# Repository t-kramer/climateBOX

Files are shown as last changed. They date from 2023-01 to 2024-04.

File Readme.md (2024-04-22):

# Welcome to the climateBOX GitHub page!

The climateBOX is a low-cost unit for personal thermal comfort monitoring.<br>
<br>
With this project we specifically aim to support novices in the field of microelectronics and help you to use the potential of low-cost sensors.<br>
<br>
Things you can find here include:

- full documentation, incl. source files for [program code](./code), [PCB](./pcb) & [housing elements](./housing)
- [building instructions](instructions.md), incl. videos
- [calibration app](https://t-kramer-revc-calibration-tool-main-mtgpng.streamlit.app) & [data](./revC-calibration) for revC velocity sensor
<br>

Also, make sure that you head to the discussions page.

https://github.com/t-kramer/climateBOX/discussions

This is where we post about any updates, ask for your feedback and host our Q&A page.<br>
<br>
<br>

Have fun!
<br>
<br>
<br>

For more information, feel free to read a scientific publication covering our thoughts around the unit's development and calibration.

*Kramer, T., Garcia-Hansen, V., & Omrani, S. (2023). climateBOX: a low-cost and open-source monitoring device for personal thermal comfort evaluation. Energy and Buildings, 112830.* https://doi.org/https://doi.org/10.1016/j.enbuild.2023.112830 



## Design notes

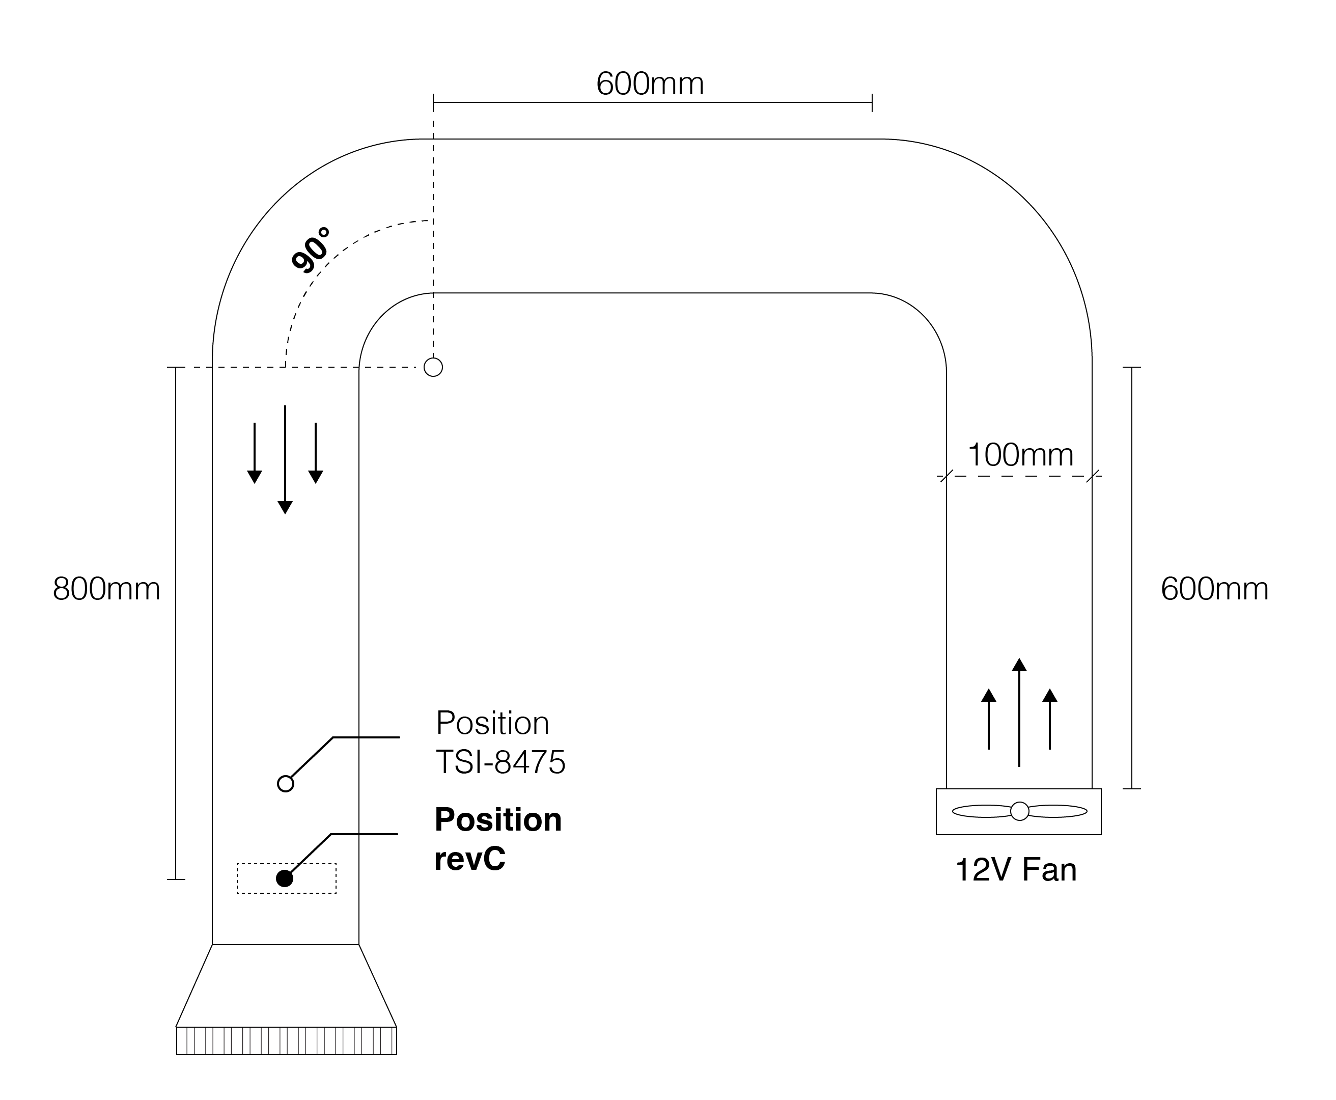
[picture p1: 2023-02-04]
img/tunnel-plan.png

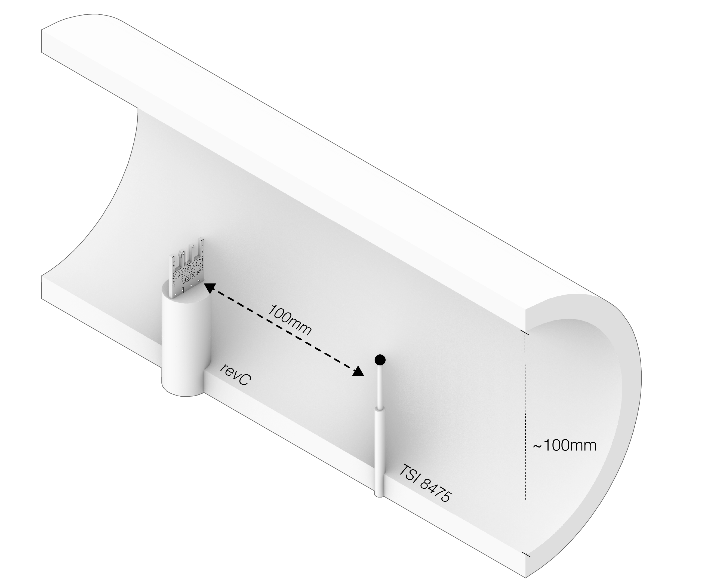
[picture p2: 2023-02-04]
img/tunnel-section.png

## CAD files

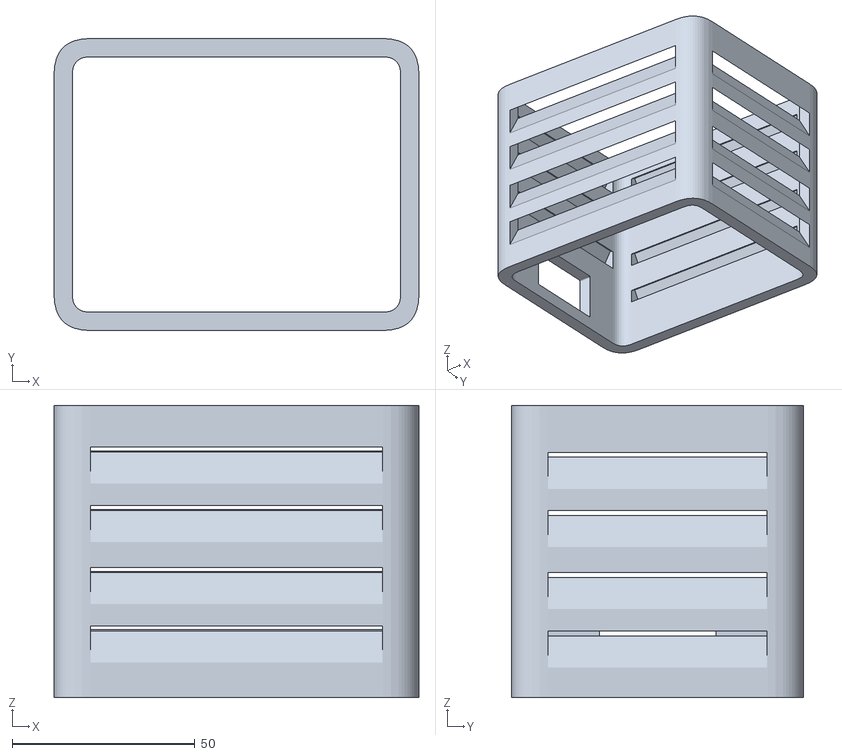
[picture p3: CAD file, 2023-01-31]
housing/stl/main-element.stl
100.0 x 80.0 x 80.0

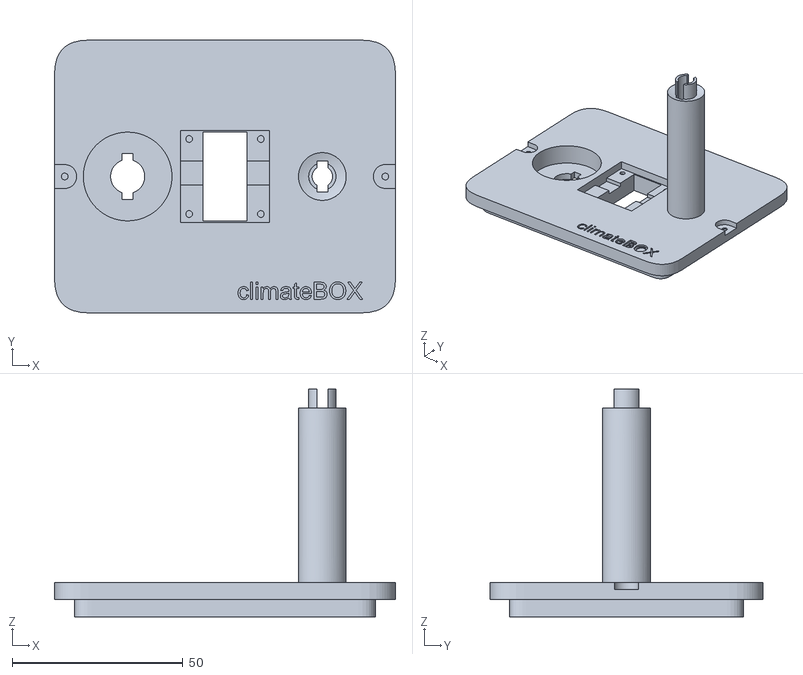
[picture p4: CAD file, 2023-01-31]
housing/stl/top-element.stl
100.0 x 80.0 x 66.7

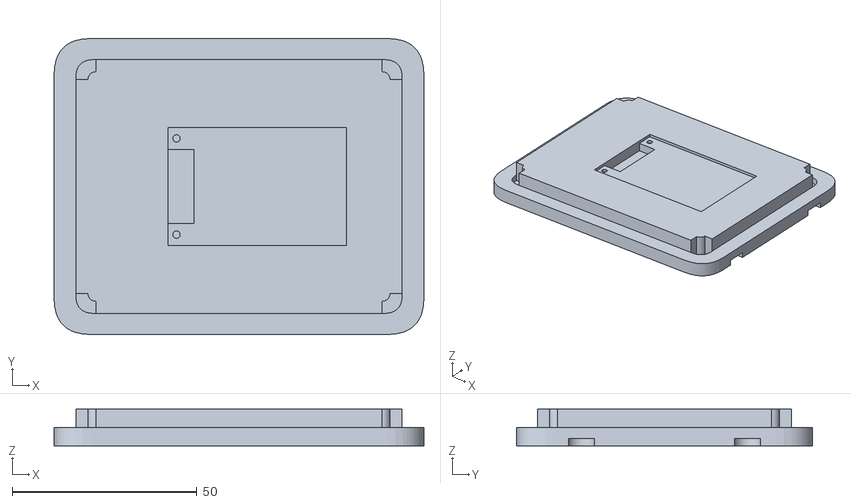
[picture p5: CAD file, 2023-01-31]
housing/stl/bottom-element.stl
100.0 x 80.0 x 10.0

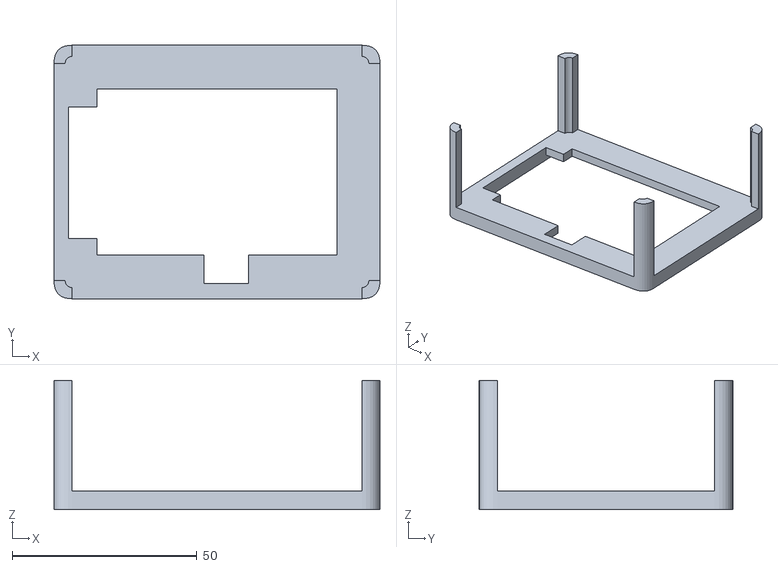
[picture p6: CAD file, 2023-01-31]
housing/stl/pcb-podest.stl
88.2 x 68.6 x 35.0

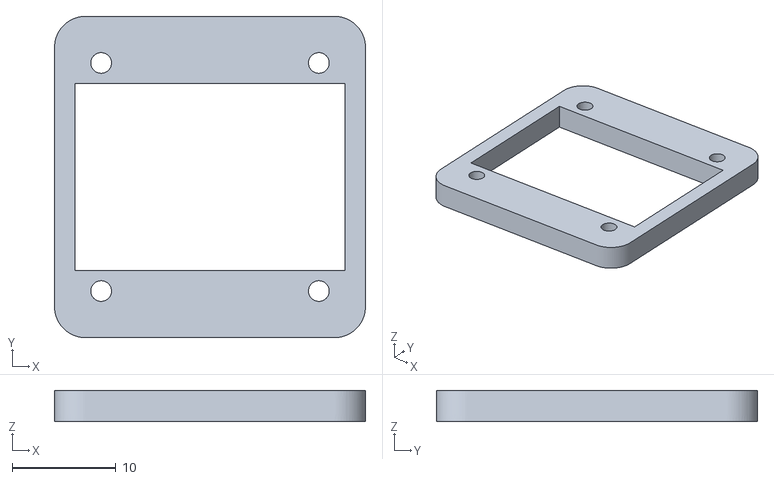
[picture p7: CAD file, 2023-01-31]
housing/stl/display-bracket.stl
30.0 x 31.0 x 3.00

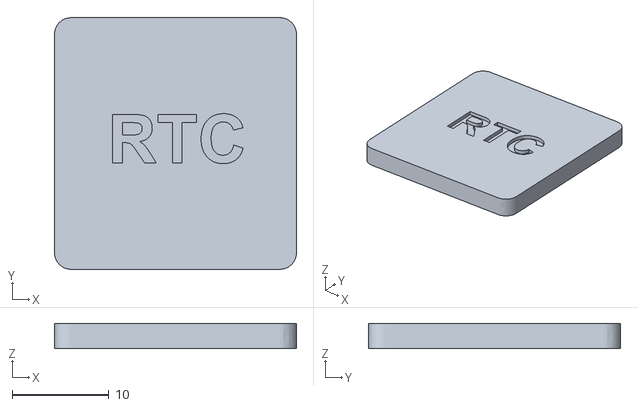
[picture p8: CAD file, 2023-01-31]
housing/stl/display-dummy.stl
25.0 x 26.0 x 2.60

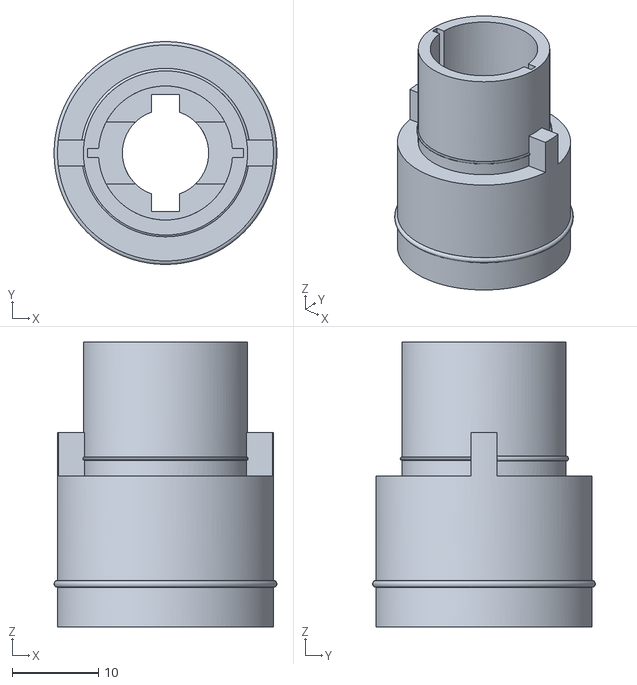
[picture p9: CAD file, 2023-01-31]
housing/stl/revC-protector.stl
25.8 x 25.8 x 33.0

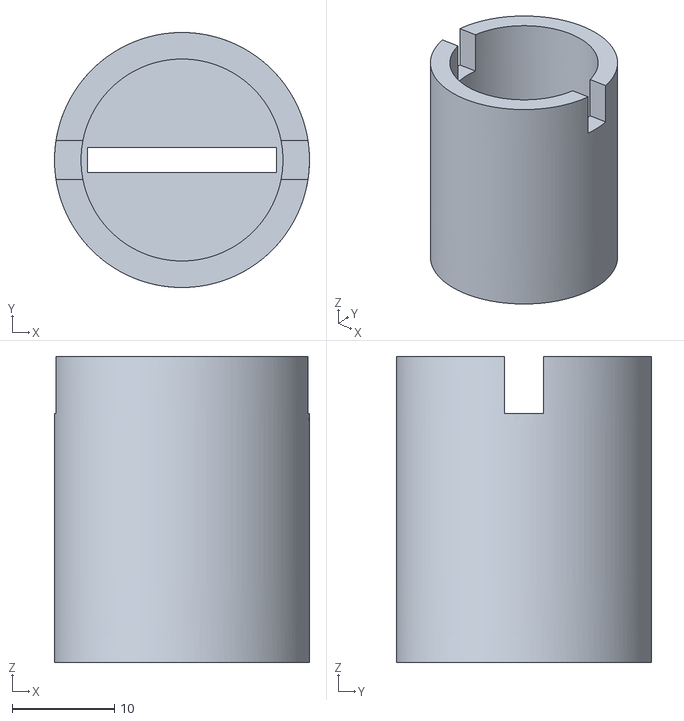
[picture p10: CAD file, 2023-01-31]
housing/stl/revc-cover.stl
25.0 x 25.0 x 30.0

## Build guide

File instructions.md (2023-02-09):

# climateBOX Building Instructions

# List of components
### a. Electronics
  1x ESP32 DevKit<br>
  1x [PCB](./pcb)<br>
  1x DHT-22<br>
  1x DS18B20<br>
  1x revC [Modern Device](https://moderndevice.com/products/wind-sensor) <br>
  1x SD module<br>
  1x RTC module*<br>
  1x OLED display*<br>
  4x 10k Ohm resistors<br>
  2x 15k Ohm resistors<br>
  1x SD card/microSD card with adapter
  1x standard micro-USB cable<br>
  1x standard 5V wall charging adapter**<br>



<br>
  
### b. Consumables
  - solder
  - stranded Wire (e.g. 22 AWG); potentially in multiple colors
  - solid core wire*
  - feather stacking headers, female
  - breakaway headers, male
  - crimp connectors + housing
  - heat shrink tubes*
  - solder wick / solder vaccuum
    

  
### c. Housing
  1x main element (side walls)<br>
  1x bottom element<br>
  1x top element<br>
  1x PCB frame<br>
  1x revC socket<br>
  1x revC cover<br>
  1x ping-pong ball, matt-black<br>
  1x display dummy* (only for v0.0)<br>
  
  [Here to Housing parts!](./housing)
  
 
  <br>

### d. Equipment
  - soldering Iron<br>
  - screw driver<br>
  - drill*<br>
  - crimping tool* (non-essential, but recommended)<br>
  - super glue*<br>

<br>
<br>
  
### e. Pre-requisites
**a) Order components**

You will not be able to build the climateBOX without the necessary components. Please stick to component list above and order them online. I can personally recommend two stores:

- https://core-electronics.com.au - Core Electronics is a good choice; generally a bit pricier, but quality equipment and fast delivery <br>
- https://au.banggood.com - Banggood is another store I can recommend; they ship internationally and are usually much cheaper; delivery takes some time though <br>

If you have questions about the components and have problems getting hands on them, feel free to send us a message and or use the discussions page. We are happy to help!
<br>
<br>

**b) Order the PCB(s)**

Before you can start building and using the climateBOX, you need to order the PCBs, or printed circuit boards. You find all require files in the [PCB](./pcb) folder

I recommend pages like https://jlcpcb.com. There are many alternatives and usually they follow the same process. You just upload the PCB files, also called “Gerber” files. This will provide the manufacturer with all essential information. You can then specify the quantity of PCBs you want to order and can make some custom configurations like changing the colour of the board etc. The price per board should be less than 2 USD.<br>
Please check the following configurations before you order:
-	Dimensions: 80mm x 60mm
-	Layers: 2

Otherwise, you should be ready to go!

*Also, if you are in Australia, feel free to contact us. We have some PCBs left and can post them.*
<br>
<br>

**c) Install Arduino IDE**

The Arduino IDE is the software we are going to use to upload the climateBOX code to the microcontroller. If you want, you can install the software before you get started with the assembly. More information can be found further below in **PART III** of the instructions.
<br>
Also, for newbies, here is a collection of useful links and tutorials that will help you with some essential vocabulary, explanations, and techniques. We will update this selection along the way.

soldering:<br>
https://core-electronics.com.au/guides/soldering-101/

stripping:<br>
https://learn.sparkfun.com/tutorials/working-with-wire/how-to-strip-a-wire

tinning:<br>
https://learn.sparkfun.com/tutorials/working-with-wire/how-to-strip-a-wire

crimping:<br>
https://core-electronics.com.au/guides/prototyping/how-to-crimp-custom-connectors/

stranded vs solid core wire:<br>
https://learn.sparkfun.com/tutorials/working-with-wire/stranded-vs-solid-core-wire

'art' of desoldering:<br>
https://www.instructables.com/How-to-Desolder-Headers/

Arduino IDE:<br>
https://core-electronics.com.au/guides/arduino-ide-tutorial/

installing ESP32 board to Arduino IDE:<br>
https://randomnerdtutorials.com/installing-the-esp32-board-in-arduino-ide-windows-instructions/
https://www.arduino.cc/en/software

installing Arduino libraries:<br>
https://docs.arduino.cc/software/ide-v1/tutorials/installing-libraries

upload program to microcontroller:<br>
https://support.arduino.cc/hc/en-us/articles/4733418441116-Upload-a-sketch-in-Arduino-IDE

<br>
<br>
<br>

  ----------------------------------
  # Step-by-Step Instructions
Now, that you hopefully have taken care of all the pre-requisites above, let’s get to the core: the actual assembly.<br>
The instructions are separated into three sections. For the first two sections, there is a helpful **video** that visualises the steps.<br> Please be aware that videos are not updated regularly and should be seen as supplementary material. **Always refer to written instructions here as the main source for documentation.**<br>
<br>
The links to the videos can be found here:<br>
<br>
[Video | Part I](https://vimeo.com/794707921)
<br>
<br>
[Video | Part II](https://vimeo.com/796140156)
<br>
<br>
Before you start, again make sure you have done the following:
- you’ve got the [PCB](./pcb)
- you have 3D-printed the [housing parts](./housing)
- you have all the components, consumables and equipment required (here we have given an asterisk * to non-essential items in the lists above)
<br>
Below you can see the circuit diagram, your main resource for building the climateBOX. Please be aware, that for v0.0 you can simply swap the OLED display for the RTC module. Both components uses the same interfaces.
<br>
circuit-diagram
<br>
The ESP32 as the microcontroller is the heart of the device. Three sensors (DHT-22, DS18B20, revC) and two additional components (SD module, OLED display/RTC module) are connected to the ESP32. Both the DHT-22 and DS18B20 require a pull-up resistor (R5, R6). As you can see, the diagram for the revC looks a bit more complicated. Here we need to do some level shifting. The revC requires around 5V to operate and provides an output signal in the same range. The ESP32 however runs on 3.3V. So to be able to use the revC output, we need to bring it down to the ESP32 operating range.
<br>
Download here:<br>
<br>
[schematic-v1.1.pdf](https://github.com/t-kramer/climateBOX/files/10541439/schematic-v1.1.pdf)

## PART I: Preparing the PCB
  
#### PCB Overview
  
<br> 

<br>
The printed circuit board (PCB) is the heart of the climateBOX. All components will be connected to the PCB, either directly soldered or via headers. We decided to use a hybrid approach in which we used headers for the sensors and the direct solder connection for other components. The obvious advantage of headers is that it is a lot easier to attach and detach components during assembly and in the case that a component needs to be replaced.<br>
<br>
The following instructions will roughly follow the order shown in the video. It is best to follow both the written instructions and the video, especially when you are new to microelectronics.<br>
<br>

**NOTE: This part is covered in video ‘climateBOX - PART I’**

<br>
Here's the link to the video again:
<br>

[Video | Part I](https://vimeo.com/794707921)

<br>
  
#### 1.1 Attaching the resistors to PCB
The first step is to attach the six resistors (4x10k Ohm,2x15k Ohm) to the PCB. For each resistor, thread both ends through the dedicated ‘through holes’ from the top side of the PCB. Then, turn the board around and fix the resistors by soldering both ends to the board.<br>
<br>
  
<br> -- IMAGE -- <br>
  
#### 1.2 Attaching female feather headers to PCB
Next, you can attach the female feather headers for the ESP32 to the PCB. Alternatively, you could also directly solder ESP32 to the PCB. However, like explained before, using headers will simplify the disassembly in case of component errors or other problems.<br>
<br>
  
<br> -- IMAGE -- <br>
  
#### 1.3 Attaching male headers to PCB
Like in the previous step, for revC and DS18b20 we opted for the flexible solution of not directly soldering these sensors or their wire ends to the PCB, but to use headers instead. In this case we used the combination of male headers on the PCB side and crimped female connecters on the sensor side. More about that in Section 2. So go ahead and solder the male pin headers to the PCB.<br>
<br>
  
<br> -- IMAGE -- <br>
  
#### 1.4 DHT-22
If you want, you can also solder the DHT-22 to the PCB directly by using the dedicated holes in the middle of the PCB. You can also use female feather headers. This will give you more flexibility when attaching/detaching the sensor.<br>
<br>

#### 1.5 RTC | Display module
Attention: If you opted for v1.0 that uses the display, I do recommend adding another set of male pin headers to the PCB. This will facilitate the assembly of climateBOX v1.0 later. This step is not covered in the video but follows the same procedure.<br>
<br>
That’s all you have to do to prepare the PCB. Next, let’s take care of the individual components and prepare them for assembly.<br>
<br>
<br>
  
## PART II: Preparing components
The following components are covered in this section:
-	globe temperature sensor (DS18B20)
-	air velocity sensor (revC)
-	SD module
<br>
Depending on the version you want to build, you have to add one additional component to this list. If you are going for v0.0, you have to prepare the RTC module. Otherwise, if you are going for v1.0, prepare the display module. Since the preparation of both modules pretty much follows the same steps covered earlier in this section, we do not cover them in the video. But you should have enough practice from previous steps to prepare these components without visual instructions.<br>
<br>

**NOTE: This part is covered in video ‘climateBOX - PART II’**

The link to the video can be found here:
<br>

[Video | Part II](https://vimeo.com/796140156)

<br>
<br>

#### 2.1 DS18B20
The DS18b20 usually comes with a relatively long cable containing three wires for power (red), ground (black) and data (white). We recommend shortening the cables/wires to around 150mm. But be careful here not to remove too much. The sensor/globe thermometer of the climateBOX sits on top of a small pole. The length of the pole needs to be included in the cable length, otherwise the cable won't be long enough, and you cannot connect it to the PCB.
<br>
  
   <br> -- IMAGE -- <br>
  
<br>
Now, after you have shortened the wires, it is time to attach the female crimp connectors. But before you can proceed you need to get rid of some insulation to expose the wires, a process called stripping. If you have never stripped a wire before, this might be of help:
<br>
https://learn.sparkfun.com/tutorials/working-with-wire/how-to-strip-a-wire
<br>
  
   <br> -- IMAGE -- <br>
  
<br>
After removing the insulation for both the main cable and the individual wires, the crimping connectors can be attached to the three wires using a crimping tool. Here, you should have a few trial runs before you actually start using the crimp connectors on the DS18B20. Again, here is a helpful link that can get you started:<br>
<br>
https://core-electronics.com.au/guides/prototyping/how-to-crimp-custom-connectors/
<br>
  
   <br> -- IMAGE -- <br>
  
  <br>
If you are satisfied with your crimping skills, go ahead apply them on the three wires.<br>
<br>
If you like it neat and tidy like me, now is the time to use some heat shrink tube to protect the exposed wires.<br>
<br>
When you are done, push the female connectors into the housing. Here, make sure that you keep the wires in the right order and that the crimped connectors are pushed deep enough into the housing until they click in properly. But be careful, as soon the connectors are locked in it can be quite hard to get them out again without breaking the plastic housing.<br>
<br>
Then you can use a hairdryer to apply the heat shrink. Done!<br>
<br>

<br> -- IMAGE -- <br>

<br>

#### 2.2 revC
Now it's time to prepare the revC. Here, we are using only four of the five pins: GND, TMP, RV, +V.<br>
<br>
The first step here is cut four wires (I recommend stranded wire, AWG22) to a length of approximately 100 mm.<br>
<br>

<br> -- IMAGE -- <br>

Stranded wire is best here because it will be exposed to some bending. Stranded wire is more flexible and is generally the best choice for most internal components.<br>
<br>
Read more about the difference between strand and solid core wire [here](https://learn.sparkfun.com/tutorials/working-with-wire/stranded-vs-solid-core-wire):
<br>
<br>
Also, colour coding makes sense here. If you have wire of different colours go ahead and use them. In the example, we used black/GND, red/V+, yellow/RV and green/TMP.<br>
<br>

<br> -- IMAGE -- <br>

Then, you can strip both ends of the wires.<br>
<br>
On one end of each wire, a female crimp connector will be attached. Here, you can go through the same process we described earlier: stripping, crimping female connectors, pushing connectors into the housing.<br>
<br>
On the other end, we need to the tin the stranded wire. The process of tinning is described under the same [link](https://learn.sparkfun.com/tutorials/working-with-wire/how-to-strip-a-wire) we used earlier.<br>
<br>
After you've completed these steps, make sure that all wires have approximately the same length. This is important for the next step. You can use a side cutter to adjust the length of the tinned wire ends.
Also, you can go ahead slip over some heat shrink over each wire. Like previously, that will later protect the soldered connections.<br>
<br>	
Now you can solder the prepared wires to the actual revC module. In the final climateBOX unit, the revC is positioned upright in a special socket (part 6+7 in the explosion graphic). Therefore, you shouldn't follow the usual process of using the through holes for the soldering connection. If you do that, the wires will be attached in a 90° angle. The socket doesn't provide enough space for that and there would be too much strain on the wire-sensor connection. Here, we will use an alternative method that allows use to solder the wires "in-parallel", which is more space-efficient in this scenario.<br>
<br>
To do that, we start by applying a big drop of solder to the solder pads to "fill" them. The solder needs to fully cover each solder pad we use, you can be generous here. Then, wire for wire, you reheat the "solder-drop" and gently push the tinned wire-ends into the melted solder drop and let it cool down to fix the connection. In the end, you only need to heat the heat shrink tubes for protection (if using). Voila, we've got ourselves a good and reliable connection.<br>
<br>
Next step SD module!
<br>
<br>

  #### 2.3 SD Module
For the SD card module the procedure is a bit different. Here we recommended a direct, non-detachable connection between SD module and PCB. Housing and PCB are designed in a way that the SD module is positioned directly under the PCB. This means we can use solid core wire, which does not need to be very flexible and saves the effort of tinning.<br>
<br>
Before you cut the wires to a length of ~40 mm, make sure that you remove any pre-installed pins from the SD module. The clean removal of pre-installed pins can be an art itself and you need to very careful here not to damage the rest of the module. [This](https://www.instructables.com/How-to-Desolder-Headers/) might be a good resource if you haven't done something like that before.
<br>
<br>
Then the process is a bit different. It makes sense to watch the video first before you go ahead, just to get the strategy. I recommend the following approach:<br>
<br>
Start and solder one end of each wire to the cleaned SD module.<br>

<br> -- IMAGE -- <br>

Then slip over some heat shrink and lead the SD module wires through the dedicated through holes on the PCB as if you were preparing to solder.<br>
<br>
After that, still keeping both components together, try to cautiously put down the PCB and SD module in the prepared housing elements. Make sure that everything is in its correct place, especially the SD module should nicely fit into the designated cavity.<br>

<br> -- IMAGE -- <br>

Now, for each through hole there should appear some remaining wire on the top side of the PCB. If this is the case, and everything is still in position, you can go ahead and solder. Afterwards, you should have some connecting wires of exactly the length you need. The last step is to use scissors or a side cutter to get rid of protruding wire on the top of PCB and apply the heat shrink below to protect the connection.<br>
<br>
<br>
<br>

  #### 2.4 RTC/Display module
Now it is time for the last component. Like we explained earlier, the component you use depends on the climateBOX version you want to build:<br>
<br>
V0.0 -> RTC<br>
<br>
V1.0 -> OLED display<br>
<br>
We can use either of these modules because they use the same PCB pins to communicate with the microcontroller.<br>
<br>
The process for both modules is roughly the same. However, we’d recommend the following: If building v0.0, directly solder the wired RTC to the bottom of the PCB. For v1.0 we use the proven combination of male header pins and female crimp connectors. We’ll quickly describe both alternatives below. But first, make sure to remove any previously installed header pins on the module you are going to use.<br>
<br>

**OLED display v1.0**

The preparation here is very similar to the revC sensor. You have to go through the process of cutting wires (AWG-22, length: ~ 100 mm), tinning (one end of each wire) and crimping (other end of the wire).<br>
<br>
After that, you can go ahead and solder the tinned ends of the wires to the OLED display module.<br>
<br>
Then push over some heat shrink if you like. Now, you can push the crimped connectors into the housing. Voila, you are done with the preparations and can assemble everything in **PART III**.<br>
<br>
<br>

**RTC v0.0**

The first steps for the RTC are similar to the ones above: cutting wires (AWG-22, length: ~ 100 mm) and tinning (both ends of each wire).<br>
<br>
Because we are going for a fixed solution here, where the RTC module is directly soldered to the PCB instead of using the detachable female connector, we save ourselves the crimping process. Just beware that a potential removal or exchange of this module later might be a bit of a tedious procedure.<br>
<br>
After tinning both wire ends, you can go ahead and solder one end of each wire to the RTC module, done! The rest will be covered in PART III.<br>
<br>
<br>

## PART III: Preparing the housing

<br>
All housing parts can be 3D printed by using the .stl files in the [housing](./housing) folder.<br>
<br>
<br>
When printed, you should go ahead and check every part for potential printing errors and test-assemble everything. The explosion graphic below shows you how to do that. 
<br>
<br>

<br>
<br>
In both, bottom and top element, there are notches. Later on, these notches accommodate a pair of screws that hold together the whole unit. We recommend to pre-drill the holes here. This will simplify the screwing process later.<br>
<br>
After you’ve done that, you can go ahead with the actual assembly.<br>
<br>
<br>

## PART IV: Assembly
Now that you've prepared all parts and finished most of the work, it's time to put everything together. <br>
<br>
But before you proceed with the final assembly and put everything into the housing, it makes sense to test the climateBOX core and its connections (soldered/crimped) before. So, I recommend dividing the assembly into two steps:
<br>

-	core assembly
-	final assembly

<br>
  
  [PICTURE]
 
#### 4.1 Core assembly
First, solder all components which do not use crimped connectors and have not been attached to the PCB yet (e.g. RTC*, DHT*) to the board. If you have followed all steps until here, you should have done that already.<br>
<br>
For the components using crimped connectors (e.g. revC, DS18b20, OLED*), you can now go ahead and attach the prepared components via the male pins previously soldered to the PCB.<br>
<br>
A quick summary of the steps and my recommended connection in brackets:
-	attach DHT-22 to PCB (soldered OR female feather headers)
-	attach DS18b20 sensor to PCB (crimped connection using male pin headers)
-	attach revC sensor to PCB (crimped connection using male pin headers)
-	v0.0: attach RTC module to PCB (directly soldered to PCB)
-	v1.0: attach OLED display module to PCB (crimped connection using male pin headers)
-	make sure SD module is soldered to PCB and SD card is inserted
-	attach ESP32 (female feather headers)

#### 4.2 Connection test
  
#### 4.2.1 The Arduino IDE
Before you go ahead with the final assembly and put everything into the housing, it makes sense to test your core connections and make sure that everything works as expected. To do that, we need to upload the climateBOX program to the ESP32 board. This can be done using the Arduino IDE, a software that allows to write and send code to the microcontroller via USB. If haven't heard about Arduino, the web has a lot of fantastic resources to dig a little deeper. The Arduino IDE is briefly described [here](https://core-electronics.com.au/guides/arduino-ide-tutorial/).
<br>
<br>
So, depending on your operating system you should head to the official Arduino website and download the IDE for Windows or Mac.<br>
<br>
https://www.arduino.cc/en/software<br>

   #### 4.2.2 Adding the ESP32 board
   The software was originally written for Arduino boards, but it does also work with the ESP32. The only thing we need to do is to manually add the ESP32 board to the board library. The following source shows you how to do that:<br>
   https://randomnerdtutorials.com/installing-the-esp32-board-in-arduino-ide-windows-instructions/<br>

 #### 4.2.3 Required libraries
To use the sensors, you also need to install some custom libraries first. Again, here is a [link](https://docs.arduino.cc/software/ide-v1/tutorials/installing-libraries) that will show you how to do that.<br>
<br>
If you are familiar with the process of installing additional libraries, please go ahead and install the following libs required to run the climateBOX:
<br>
<br>

|   Library                 | Developer         |used in:|
|---------------------------|-------------------|--------|
|   DHT sensor library      | Adafruit          | both   |
|   Adafruit Unified Sensor | Adafruit          | both   |
|   Adafruit BusIO          | Adafruit          | both   |
|   OneWire                 | Paul Stoffregen   | both   |
|   DallasTemperature       | Miles Burton      | both   |
|   RTClib                  | Adafruit          | v0.0   |
|   Adafruit SSD1306        | Adafruit          | v1.0   |
|   Adafruit GFX Library    | Adafruit          | v1.0   |
|   ESP32Time               | fbiego            | v1.0   |
|   EspMQTTClient           | Patrick Lapointe  | v1.0   |
|   PubSubClient            | Nick O’Leary      | v1.0   |

<br>
<br>

You can simply search for the name in the Arduino IDE library manager and if you are still unsure, also knowing the developer should make it easier.

<br>
<br>

  #### 4.2.4 Test Connection
Now, that all libraries are installed, the last thing we need to do upload the climateBOX program. Again, here the program you have to use depends on the climateBOX version you want to build. The programs can be found in the [code](./code) folder in this repository.<br>

<br>

If you haven’t uploaded a program to a microcontroller via the Arduino IDE yet, this [link](https://support.arduino.cc/hc/en-us/articles/4733418441116-Upload-a-sketch-in-Arduino-IDE) might be of help.
<br>
<br>

But before you upload the code to test your core assembly, it might be worth an excursion to the next section where I explain the program codes and their differences.<br>

<br>

When you have gone through the information in the next section, use the electrical circuit diagram to check all your connections once again and make sure you have connected all components in the right way.<br>

<br>

If you are confident that everything is in its correct spot, you can go ahead and connect your assembled PCB core to the computer via USB.<br>

<br>

Following the instructions in the provided link, make sure that you have selected the right board (DOIT ESP32 DEVKIT V1) and the correct port.<br>

<br>

If everything is connected properly, the core device should work as expected and described in the program code section. You can now continue with the final assembly.<br>

<br>

Otherwise, if you are having problems, first check the following, common issues:<br>
Properly check all the connections for:<br>

<br>

-	Badly soldered connections
-	Loose connections, e.g. crimp connectors not properly attached to pins
-	Component attached in a wrong way
-	Wires attached in wrong order
-	SD not inserted
-	RTC is missing battery

<br>
<br>

If neither of those things fixes your problem, feel free to navigate to the discussion page and ask. 

<br>
<br>

  #### 4.3 Final assembly
  - detach DS18b20 & revC
  - lead wires of both sensors through pre-cut holes in top element
  - click PCB with SD and RTC module into PCB podest
  - click PCB frame element into pre-cut holes in bottom element (maybe use super glue to fix connections)
  - click in DHT22 sensor into PCB designated feather headers (if not soldered)
  - slip over main wall element
  - lift top element including revC and DS18b20 sensors
  - connect sensors to PCB
  - while pushing wires into the interior of the box, push down the top element and attach by tightening screws
  - attach USB wires

<br>

assembly@2x

--------------------------------------------------
  ## Part V: The Program Code
  
  We are planning to release another video here soon.<br>
  The video will cover the following:<br>
  - general code structure
  - differences between v0.0 and v1.0
  - how to set-up a cloud monitoring system consisting of several v1.0 climateBOX units
  - FAQ, common errors and further information on things like resetting the RTC, customisations, etc.
  <br>
  <br>
  For now, please refer to the inline comments in the sketches/program files. Also, feel free to contact us if there is anything specific you want to know. :)
  <br>
  <br>
  For v0.0: If you have manually installed all libraries mentioned above, you should be able to upload and run the code without any prior knowledge and further explanations. Before you upload the code, make sure that you change the zeroWind adjustment to the value you obtained from the calibration/calibration tool. Otherwise, if you have followed the steps described earlier and the reminders below, you should be ready to go.
  
  <br>
  <br>

  - make sure that: USB wire is attached properly, SD card is inserted
  - connect climateBOX to PC/Mac via USB
  - select the correct board in Arduino IDE
  - verify and upload the climateBOX_v0.0.ino file
  - check the serial monitor for output

--------------------------------------------------
  ## OPTIONAL - Part VI: Setting up a cloud-based monitoring system (advanced)
  
  The ESP32 comes with on-board WiFi. This allows to use several v1.0 units together in a WiFi-based monitoring system with live data upload to a cloud database and/or dashboard. This facilitates the process of retrieving the data and a provides a live visualisation of collected data. Please be aware, that the v1.0 work individually without a problem and do only require WiFi access to update the time. The data is always stored on the local SD card. But who doesn't want a nice and schmick dashboard?
  <br>
  <br>
  What you need:
  <br>
  1x Raspberry Pi (e.g. 3 or 4)
  <br>
  1x 4G/LTE USB Dongle incl. SIM card from your local mobile provider
  <br>
  2+ climateBOX v1.0 units
  <br>
  
  <br>
  <br>
  
  In a minimal solution, the only things you need are a climateBOX v1.0 unit and a WiFi network. Services like Adafruit I/O make it very easy to upload microcontroller data to a live dashboard and do not really require any background knowledge. If you think that this is your preferred option, feel free to do some research on the web. There are many sources that describe how to set up such a system. Hint: The Adafruit I/O webpage would be a good start :)
  However, based on our experience we suggest an alternative solution which, to be honest, requires a little more setup, but is absolutely worth the effort.
  
  <br>
  <br>
  
  In todays world where most WiFi networks are well protected, it can be quite hard to connect your microcontrollers, especially if you want to use it for a longer period and don't want to change network SSIDs and PW everytime you setup your device in a new space. This is why we suggest to make your system completely indepedent and to bring your own network. Yes, correct. You can easily bring your own network with you.
  
  <br>
  <br>
  
  We made good experiences with using a Raspberry Pi and a common 4G USB dongle to setup our own network. Connected to the 4G/LTE mobile network via a SIM card from a local provider, the RPi acts as a hotspot all your units can be connected to. The best thing is that the IP address, network SSID and PW remain the same, wherever you want to go. This means that setting up your system in a new place is as easy as connecting everything to a power source, done!
  
  <br>
  <br>
  
  While setting up the communication between the climateBOX units, RPi and the web might take some time, this remains an initial one-time effort and usually doesn't require any maintenance or updates. The most difficult part is probably to setup the RPi. Luckily, someone made an effort to explain everything step by step:
  
  <br>
 
  LINK
  
  <br>
  <br>
  
  If you want a little more background information, it might be worth reading about [MQTT](https://mqtt.org), the communication protocoll that is used here. In our system the RPi is the MQTT broker, and the individual climateBOX units are clients. The climateBOX v1.0 code is written for use in such a system. The only things you need to adjust are the settings related to the MQTT. More on that in the additional video which will be released soon.

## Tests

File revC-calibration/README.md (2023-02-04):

Welcome to the **revC calibration** folder!

In here, you'll find two things:<br>
<br>
a) raw data gathered for the calibration of our sensors<br>
b) the **revC calibration app**
<br>
<br>
The most important thing for you will be the calibration app, which will assist you in calibrating each revC sensor you are using against a reference function.
The app is based on another repository and can be found deployed as a Streamlit app here [HERE](https://t-kramer-revc-calibration-tool-main-mtgpng.streamlit.app)!
<br>
<br>
On this page you will also find some more information about the process.

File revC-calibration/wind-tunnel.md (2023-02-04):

### Wind tunnel

To construct the wind tunnel we used some standard PVC pipes from the hardware store. The air movement was created by a simple 12V CPU with a variable DC supply to control the air speed. We are able to produce velocities of up to 2.4 m/s.

Here are some images of the concept:

tunnel-plan
tunnel-section

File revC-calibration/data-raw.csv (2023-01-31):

sensor-id | temp [¡C] | revC_raw_tmp | revC_raw_rv | tsi_value [m/s]
11 | 24 | 1.495 | 1.134 | 0
11 | 24 | 1.501 | 1.136 | 0
11 | 24 | 1.495 | 1.133 | 0
11 | 24 | 1.501 | 1.131 | 0
11 | 24 | 1.498 | 1.135 | 0
11 | 24 | 1.496 | 1.134 | 0
11 | 24 | 1.495 | 1.131 | 0
11 | 24 | 1.498 | 1.131 | 0
11 | 23.9 | 1.501 | 1.133 | 0
11 | 23.9 | 1.497 | 1.134 | 0
11 | 24 | 1.491 | 1.135 | 0
11 | 24 | 1.491 | 1.134 | 0
11 | 24 | 1.495 | 1.134 | 0
11 | 24 | 1.495 | 1.128 | 0
11 | 24 | 1.491 | 1.136 | 0
11 | 24 | 1.491 | 1.133 | 0
11 | 24 | 1.491 | 1.137 | 0
11 | 24 | 1.497 | 1.142 | 0
11 | 24 | 1.497 | 1.137 | 0
11 | 24 | 1.495 | 1.136 | 0
11 | 24 | 1.495 | 1.131 | 0
11 | 24 | 1.495 | 1.126 | 0
11 | 24 | 1.494 | 1.129 | 0
11 | 24 | 1.494 | 1.126 | 0
11 | 24 | 1.489 | 1.129 | 0
11 | 24 | 1.491 | 1.131 | 0
11 | 24 | 1.493 | 1.134 | 0
11 | 24 | 1.49 | 1.134 | 0
11 | 24 | 1.488 | 1.131 | 0
11 | 24 | 1.488 | 1.127 | 0
11 | 24 | 1.488 | 1.131 | 0
11 | 24 | 1.486 | 1.134 | 0
11 | 24 | 1.488 | 1.139 | 0
11 | 24 | 1.487 | 1.143 | 0
11 | 24 | 1.487 | 1.136 | 0
11 | 24 | 1.488 | 1.138 | 0
11 | 24 | 1.488 | 1.136 | 0
11 | 24 | 1.486 | 1.134 | 0
11 | 24 | 1.488 | 1.134 | 0
11 | 24 | 1.486 | 1.131 | 0
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

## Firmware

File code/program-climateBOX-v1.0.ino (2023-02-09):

/* climateBOX - Indoor climate monitoring station


-- NTP-Version (WiFi connection required) --

 This program was developed for the use on ESP32 microcontrollers (DOIT ESP32 DEVKIT V1).
 The following components are used:

  a) DHT-22                   Air temperature, relative humidity
  b) DS18B20                  Globe temperature
  c) Modern Device revC       Air velocity
  d) SD card module           -
  e) SSD1306                  0.96" OLED display


More information about the climateBOX can be found here:

- Publication:
Kramer, T., Garcia-Hansen, V., & Omrani, S. (2023). 
climateBOX: a low-cost and open-source monitoring device for personal thermal comfort evaluation. 
Energy and Buildings, 112830.

- GitHub page:
https://github.com/t-kramer/climateBOX


The code is provided by:

School of Architecture & Built Environment,
Queensland University of Technology

Contact:
t.kramer@qut.edu.au

 
 License:                       */

//______________________________________LIBRARIES______________________________________//

#include <Arduino.h>
#include "DHT.h"
#include "DHT_U.h"
#include <SPI.h>
#include <SD.h>
#include <Wire.h>
#include <Adafruit_GFX.h>
#include <Adafruit_SSD1306.h>
#include <OneWire.h>
#include <DallasTemperature.h>
#include "FS.h"
#include "PubSubClient.h"
#include "WiFi.h"
#include "time.h"
#include <ESP32Time.h>

//\\//\\//\\//\\//\\//\\//\\//\\//\\//\\//\\//\\//\\//\\//\\//\\//\\//\\//\\//\\//\\//\\/



//____________________________________USER CONFIGS____________________________________//

const char* boxID = "box2";                                 // climateBOX identifier*
const double diameter = 0.04;                               // Ping-pong ball diameter
const double emissivity = 0.95;                             // depending on ping-pong ball paint
float zeroWindAdjustment = 0;                            // revC calibration variable*


// Calibration coefficients

const double C_A_velo = 0.5588;
const double C_B_velo = -1.8402;
const double C_C_velo = 1.6074;

const double C_A_temp = 1.1423;
const double C_B_temp = 8.2098;
const double C_C_temp = -15.8171;

const double C_A_humi = 0.9388;
const double C_B_humi = -0.2178;
const double C_C_humi = 14.3411;

const double C_A_globe = 1.0185;
const double C_B_globe = -0.2829;


// WiFi & MQTT
  
const char* ssid = "[YOUR NETWORK SSID]";                        // network SSID*
const char* wifi_password = "[YOUR PASSWORD]";                   // network password*

const char* mqtt_server = "[YOUR MQTT SERVER IP]";               // IP of the MQTT broker*
const char* humidity_topic = "system/box2/rh";                   // Exemplary MQTT topics*
const char* temperature_topic = "system/box2/ta";                //
const char* globe_topic = "system/box2/tg";                      //
const char* velocity_topic = "system/box2/vel";                  //
const char* mqtt_username = "[YOUR USERNAME]";                   // MQTT username*
const char* mqtt_password = "[YOUR PW]";                         // MQTT password*
const char* clientID = "[YOUR CLIENT ID]";                       // MQTT client ID*

const char* ntpServer = "pool.ntp.org";
const long gmtOffset_sec = 32400;                           // Brisbane, Australia*
const int daylightOffset_sec = 3600;

//\\//\\//\\//\\//\\//\\//\\//\\//\\//\\//\\//\\//\\//\\//\\//\\//\\//\\//\\//\\//\\//\\/



//______________________________STATIC COMPONENT CONFIGS_____________________________//

#define DHTPIN 4                                                // DHT-22
#define DHTTYPE DHT22                                           // (AM2302), AM2321
DHT dht(DHTPIN, DHTTYPE);

#define oneWireBus 15                                           // DS18B20
OneWire oneWire(oneWireBus);
DallasTemperature sensors(&oneWire);

#define analogPinForRV    34                                    // revC air anemometer  
#define analogPinForTMP   35                                    // revC thermistor

#define SCREEN_WIDTH 128                                        // OLED display width, in pixels
#define SCREEN_HEIGHT 64                                        // OLED display height, in pixels
#define OLED_RESET     -1 
Adafruit_SSD1306 display(SCREEN_WIDTH, SCREEN_HEIGHT, &Wire, OLED_RESET);

#define SD_CS 5                                                 // SD module


WiFiClient wifiClient;                                          // Initialise the WiFi and MQTT Client objects

PubSubClient client(mqtt_server, 1883, wifiClient);             // 1883 is the listener port for the Broker



ESP32Time rtc(32400);                                           // offset in seconds GMT+9



//__________________________________DYNAMIC CONFIGS__________________________________//

double tempReading = 0;
float rawTemp;

double humReading = 0;

double globeReading = 0;

double veloReading = 0;
float tmpRaw;
float tmpRawScale;
float rvRaw;
float rvRawScale;

#define uS_TO_S_FACTOR 1000000  /* Conversion factor for micro seconds to seconds */
#define TIME_TO_SLEEP  180       /* Time ESP32 will go to sleep (in seconds) */

RTC_DATA_ATTR unsigned long rememberTime;

String timer;

void print_wakeup_reason() {
    esp_sleep_wakeup_cause_t wakeup_reason;

    wakeup_reason = esp_sleep_get_wakeup_cause();

    switch (wakeup_reason) {
        case ESP_SLEEP_WAKEUP_EXT0 :
            Serial.println("Wakeup caused by external signal using RTC_IO");
            break;
        case ESP_SLEEP_WAKEUP_EXT1 :
            Serial.println("Wakeup caused by external signal using RTC_CNTL");
            break;
        case ESP_SLEEP_WAKEUP_TIMER :
            Serial.println("Wakeup caused by timer");
            break;
        case ESP_SLEEP_WAKEUP_TOUCHPAD :
            Serial.println("Wakeup caused by touchpad");
            break;
        case ESP_SLEEP_WAKEUP_ULP :
            Serial.println("Wakeup caused by ULP program");
            break;
        default :
            Serial.printf("Wakeup was not caused by deep sleep: %d\n", wakeup_reason);
            break;
    }
}

//int data_count = 0;
int wificounter = 0;




// 'climateBOX symbol', 128x64px
const unsigned char myBitmap [] PROGMEM = {
  0x00, 0x00, 0x00, 0x00, 0x00, 0x00, 0x00, 0x00, 0x00, 0x00, 0x00, 0x00, 0x00, 0x00, 0x00, 0x00, 
  0x00, 0x00, 0x00, 0x00, 0x00, 0x00, 0x00, 0x00, 0x00, 0x00, 0x00, 0x00, 0x00, 0x00, 0x00, 0x00, 
  0x00, 0x00, 0x00, 0x00, 0x00, 0x00, 0x00, 0x00, 0x00, 0x00, 0x00, 0x00, 0x00, 0x00, 0x00, 0x00, 
  0x00, 0x00, 0x00, 0x00, 0x00, 0x00, 0x00, 0x00, 0x00, 0x00, 0x00, 0x00, 0x00, 0x00, 0x00, 0x00, 
  0x00, 0x00, 0x00, 0x00, 0x00, 0x00, 0x00, 0x00, 0x00, 0x00, 0x00, 0x00, 0x00, 0x00, 0x00, 0x00, 
  0x00, 0x00, 0x00, 0x00, 0x00, 0x00, 0x00, 0x00, 0x00, 0x00, 0x00, 0x00, 0x00, 0x00, 0x00, 0x00, 
  0x00, 0x00, 0x00, 0x00, 0x00, 0x00, 0x00, 0x00, 0x00, 0x00, 0x00, 0x00, 0x00, 0x00, 0x00, 0x00, 
  0x00, 0x00, 0x00, 0x00, 0x00, 0x00, 0x00, 0x00, 0x00, 0x00, 0x00, 0x00, 0x00, 0x00, 0x00, 0x00, 
  0x00, 0x00, 0x00, 0x00, 0x00, 0x00, 0x00, 0x00, 0x00, 0x00, 0x00, 0x00, 0x00, 0x00, 0x00, 0x00, 
  0x00, 0x00, 0x0f, 0x00, 0x00, 0x00, 0x00, 0x00, 0x00, 0x00, 0x00, 0x00, 0x00, 0x00, 0x00, 0x00, 
  0x00, 0x00, 0x3f, 0x80, 0x00, 0x00, 0x00, 0x00, 0x00, 0x00, 0x00, 0x00, 0x00, 0x00, 0x00, 0x00, 
  0x00, 0x00, 0x7f, 0xc0, 0x00, 0x00, 0x00, 0x00, 0x00, 0x00, 0x00, 0x00, 0x00, 0x00, 0x00, 0x00, 
  0x00, 0x00, 0x7f, 0xe0, 0x00, 0x00, 0x00, 0x00, 0x00, 0x00, 0x00, 0x00, 0x00, 0x00, 0x00, 0x00, 
  0x00, 0x00, 0x7f, 0xe0, 0x00, 0x00, 0x00, 0x00, 0x00, 0x00, 0x00, 0x00, 0x00, 0x00, 0x00, 0x00, 
  0x00, 0x00, 0x7f, 0x20, 0x00, 0x00, 0x00, 0x00, 0x00, 0x00, 0x00, 0x00, 0x00, 0x00, 0x00, 0x00, 
  0x00, 0x00, 0x7c, 0x00, 0x00, 0x00, 0x00, 0x00, 0x00, 0x00, 0x00, 0x00, 0x00, 0x00, 0x00, 0x00, 
  0x00, 0x00, 0x20, 0x00, 0x00, 0x00, 0x00, 0x00, 0x00, 0x00, 0x00, 0x00, 0x00, 0x00, 0x00, 0x00, 
  0x00, 0x00, 0x00, 0x00, 0x00, 0x00, 0x00, 0x00, 0x00, 0x00, 0x00, 0x00, 0x00, 0x00, 0x00, 0x00, 
  0x00, 0x00, 0x00, 0x00, 0x00, 0x00, 0x00, 0x00, 0x00, 0x00, 0x00, 0x00, 0x00, 0x00, 0x00, 0x00, 
  0x00, 0x00, 0x00, 0x00, 0x00, 0x00, 0x00, 0x00, 0x00, 0x01, 0x00, 0x00, 0x00, 0x00, 0x00, 0x00, 
  0x00, 0x00, 0x04, 0x00, 0x00, 0x00, 0x00, 0x00, 0x1e, 0x03, 0x00, 0x00, 0x00, 0x00, 0x00, 0x00, 
  0x00, 0x00, 0x06, 0x00, 0x38, 0x00, 0x00, 0x00, 0x06, 0x00, 0x00, 0x00, 0x00, 0x40, 0x00, 0x00, 
  0x00, 0x00, 0x07, 0x00, 0x3c, 0x00, 0x00, 0x1d, 0x06, 0x06, 0x0d, 0x30, 0xe0, 0x40, 0x1c, 0x00, 
  0x00, 0x00, 0x07, 0x00, 0x3c, 0x00, 0x00, 0x37, 0x06, 0x03, 0x06, 0xd1, 0x91, 0xfc, 0x63, 0x00, 
  0x00, 0x00, 0x07, 0x00, 0x30, 0x00, 0x00, 0x41, 0x06, 0x01, 0x04, 0x90, 0x18, 0x40, 0x41, 0x00, 
  0x00, 0x00, 0x0e, 0xfc, 0x30, 0x00, 0x00, 0x40, 0x06, 0x01, 0x04, 0x91, 0xf8, 0x40, 0x7f, 0x00, 
  0x00, 0x00, 0x1c, 0xff, 0xf3, 0x00, 0x00, 0x40, 0x06, 0x01, 0x04, 0x92, 0x18, 0x40, 0x40, 0x00, 
  0x00, 0x00, 0x7d, 0xff, 0xf3, 0xe0, 0x00, 0x63, 0x06, 0x01, 0x04, 0x9b, 0x38, 0x66, 0x63, 0x00, 
  0x00, 0x01, 0xff, 0xf7, 0xf3, 0xc0, 0x00, 0x1c, 0x1f, 0x8f, 0xee, 0xc9, 0xcc, 0x3c, 0x3e, 0x00, 
  0x00, 0x03, 0xff, 0xff, 0xe7, 0xc0, 0x00, 0x00, 0x00, 0x00, 0x00, 0x00, 0x00, 0x00, 0x00, 0x00, 
  0x00, 0x03, 0xff, 0xff, 0xff, 0x80, 0x00, 0x00, 0x00, 0x00, 0x00, 0x00, 0x00, 0x00, 0x00, 0x00, 
  0x00, 0x03, 0xf7, 0xff, 0xff, 0x40, 0x00, 0x00, 0x00, 0x00, 0x00, 0x00, 0x00, 0x00, 0x00, 0x00, 
  0x00, 0x03, 0xff, 0xcf, 0xff, 0x40, 0x00, 0x00, 0x00, 0x00, 0x00, 0x00, 0x00, 0x00, 0x00, 0x00, 
  0x00, 0x03, 0xff, 0xff, 0x3c, 0x40, 0x07, 0xff, 0xff, 0xff, 0xff, 0xff, 0xff, 0xff, 0xff, 0xf8, 
  0x00, 0x02, 0x83, 0xff, 0xf0, 0xc0, 0x00, 0x00, 0x00, 0x00, 0x00, 0x00, 0x00, 0x00, 0x00, 0x00, 
  0x00, 0x03, 0xfc, 0x0f, 0xf0, 0xc0, 0x00, 0x00, 0x00, 0x00, 0x00, 0x00, 0x00, 0x00, 0x00, 0x00, 
  0x00, 0x03, 0xff, 0xe0, 0x31, 0xc0, 0x00, 0x00, 0x00, 0x00, 0x00, 0x00, 0x00, 0x00, 0x00, 0x00, 
  0x00, 0x00, 0x03, 0xff, 0xc1, 0x80, 0x00, 0x00, 0x00, 0x00, 0x00, 0x00, 0x00, 0x00, 0x00, 0x00, 
  0x00, 0x01, 0xf0, 0x0f, 0xf1, 0x80, 0x00, 0x00, 0x00, 0xff, 0x03, 0xe1, 0xef, 0x00, 0x00, 0x00, 
  0x00, 0x01, 0xff, 0x80, 0x31, 0x80, 0x00, 0x00, 0x00, 0x7f, 0x87, 0xf1, 0xef, 0x00, 0x00, 0x00, 
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
};







//__________________________________SAVING FUNCTION_________________________________//
void storeDataToSDCard(fs::FS &fs, const char * path, const char * message) {
  Serial.printf("Appending data to file: %s\n", path);

  File file = fs.open(path, FILE_APPEND);
  if(!file) {
    Serial.println("Failed to open file for appending");
    return;
  }
  if(file.println(message)) {
    Serial.println("Data appended");
  } else {
    Serial.println("Append failed");
  }
  file.close();
}





//__________________________________MQTT FUNCTION_________________________________//
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

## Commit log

2023-01-31 Add files via upload
    First upload of stl-files
    [bottom-element.stl, display-bracket.stl, display-dummy.stl, main-element.stl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]
2023-01-31 Add files via upload
    First upload of raw revC calibration data.
    [data-raw.csv]
2023-01-31 Update instructions.md
    Added assembly overview graphic.
